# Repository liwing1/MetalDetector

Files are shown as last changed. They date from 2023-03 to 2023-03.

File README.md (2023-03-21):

# Processo Seletivo HealthGo - Projeto Detector de Metais

# Objetivo

Projetar um detector de metais para garantir a segurança dos pacientes antes de exames.

Condições:

    - Chave liga/desliga;
    - LED de indicação de alimentação do sistema;
    - Botão para habilitar/desabilitar detecção;
    - LED de indicção de detecção habilitada;
    - Buzzer de sinalização na presença de metal.

# Hardware

O primeiro passo para a realização do projeto é montar um diagrama em alto nível de abstração:

diagrama

Com essas informações já é possível construir uma lista de componentes que será necessário para o funcionamento de cada bloco.

## 1. Regulação de Tensão

Tendo em vista que todos os componentes dependem de redução da tensão para funcionarem, foi primeiramente projetado o regulador de tensão.

power

Optou-se pela utilização do LM296 devido a sua grande disponibilidade no mercado e alta performance. Vale ainda salientar que o LED de indicação de alimentação foi posicionado após a regulação da tensão. Assim, fica evidente que os demais componentes estão sendo alimentado corretamente.

## 2. Microcontrolador

A tarefa de ler os registros de um sensor através de comunicação serial é muito simples. No entanto, por se tratar da segurança de pacientes, deve-se ser cauteloso com a escolha do processador.

uc

O ESP32-WROOM-32 foi escolhido por sua robustez tanto no hardware quanto no software.

## 3. Sensor 

O sensor indutivo foi previamente definido, incluindo a impendância indutiva que é acoplada ao chip. Para que seja atingida a frequência de ressonância de 3MHz no tanque LC, a capacitância adicionada em paralelo deve ser calculada através da equação 1 fornecida no datasheet do fabricante:

fsensor

O valor obtido foi de 390.89 pF. Entretando, o valor comercial mais próximo é de 390 pF, que está dentro da faixa de erro do próprio capacitor.

sensor

Nota-se ainda que além da comunicação serial com o microcontrolador, é necessário também o fornecimento de um sinal de clock externo que serve como referência interna para a amostragem do sinal (a recomendação do fabricante é 16MHz).

# Firmware

Da mesma forma que o hardware é separado de forma modular através de blocos funcionais, é interessante que o software mantenha a mesma estrutura. Assim, o código pode ser reaproveitado com mais facilidade.

Ademais, apesar de o Arduino ser uma das plataformas de desenvolvimento mais populares, optou-se pela utilização do framework oficial da Espressif, o ESP-IDF. Neste ambiente a inclusão de bibliotecas é mais simples graças ao CMake. Além disso a API permite um controle mais preciso sobre os periféricos.

## 1. Porte da Lib

Para importar a biblioteca fornecida ao ESP-IDF foi necessário transforma-la em um _component_ através do arquivo CMakeLists.txt:
```C
idf_component_register(SRCS "ldc1101_driver.c" "ldc1101_hal.c"
                    INCLUDE_DIRS "."
                    PRIV_REQUIRES driver)
```

Após esse passo o biblioteca ja passa a ser compilável. No entanto, por ser um código genérico para qualquer arquitetura, é necessário adicionar a camada de abstração de hardware (HAL) específica do ESP.

```C
void hal_spiMap(T_HAL_P spiObj)
{
    T_HAL_SPI_OBJ tmp = (T_HAL_SPI_OBJ)spiObj;

    spi_bus_config_t spi_bus_config = {
        .mosi_io_num = tmp->mosi_io_num,
        .miso_io_num = tmp->miso_io_num,
        .sclk_io_num = tmp->sclk_io_num,
        .quadwp_io_num = PIN_NOT_USED,
        .quadhd_io_num = PIN_NOT_USED,
        .max_transfer_sz = 32,
    };

    spi_device_interface_config_t spi_device_interface_config = {
        .mode = 2,                  //POL:1; PHA:0
        .clock_speed_hz = tmp->clk_speed_hz,
        .queue_size = 1,
        .spics_io_num = PIN_NOT_USED,
        .pre_cb = NULL,
        .post_cb = NULL,
    };

    spi_bus_initialize(SPI2_HOST, &spi_bus_config, SPI_DMA_CH_AUTO);
    spi_bus_add_device(SPI2_HOST, &spi_device_interface_config, &spi_handle);
}

void hal_spiWrite(uint8_t *pBuf, uint16_t nBytes)
{
    spi_transaction_t transaction = {
        .tx_buffer = pBuf,
        .length = nBytes
    };
    spi_device_polling_transmit(spi_handle, &transaction);
}

void hal_spiRead(uint8_t *pBuf, uint16_t nBytes)
{
    spi_transaction_t transaction = {
        .rx_buffer = pBuf,
        .length = nBytes
    };
    spi_device_polling_transmit(spi_handle, &transaction);
}
```

## 2. Inicialização
Depois de inicializar os periféricos de interação com o usuário e o clock externo, o ESP pode finalmente se comunicar com o sensor. Utilizando-se da biblioteca fornecida pela MIKROE, a configuração e leitura do sensor fica muito simplificada.

```C
void applicationInit()
{
    _LDC1101_SPI_INTERFACE spi_interface ={
        .miso_io_num = 12,
        .mosi_io_num = 13,
        .sclk_io_num = 14,
        .clk_speed_hz = 8000000,
    };
    ldc1101_spiDriverInit( (T_LDC1101_P)&spi_interface );
    ldc1101_init();

    // Valores otimizados da ref: http://www.ti.com/lit/zip/slyc137
    // RPmax = 12k; RPmin = 3k
    ldc1101_writeByte(_LDC1101_REG_CFG_RP_MEASUREMENT_DYNAMIC_RANGE,_LDC1101_RP_SET_RP_MAX_12KOhm | _LDC1101_RP_SET_RP_MIN_3KOhm);
    // C1 = 6pF; R1 = 41.63k
    ldc1101_writeByte(_LDC1101_REG_CFG_INTERNAL_TIME_CONSTANT_1,_LDC1101_TC1_C1_6pF | 0x1D);
    // C2 = 24pF; R2 = 97.5k
    ldc1101_writeByte(_LDC1101_REG_CFG_INTERNAL_TIME_CONSTANT_2,_LDC1101_TC2_C2_24pF | 0x39);
    // MINfreq = 7MHz; RESPtime = 192s
    ldc1101_writeByte(_LDC1101_REG_CFG_RP_L_CONVERSION_INTERVAL, 0xD0 | _LDC1101_DIG_CFG_RESP_TIME_192s);

    ldc1101_setPowerMode(_LDC1101_FUNC_MODE_ACTIVE_CONVERSION_MODE);
    
    ldc1101_goTo_RPmode();
    ESP_LOGW(LDC1101_TAG, "--- Start measurement ---");
}
```

## 3. Laço Principal

Graças ao FreeRTOS foi possível subdividir o programa em duas tarefas que são processadas de forma independente.

```C
void button_task(void* arg)
{
    uint32_t io_num;
    while(1)
    {
        // Entra neste if quando botão é precionado
        if(xQueueReceive(gpio_evt_queue, &io_num, portMAX_DELAY)) {
            
            sensor_state = !sensor_state; //toggle sensor

            led_set_level(sensor_state == SENSOR_OCIOSO ? LED_OFF:LED_ON);
        }
        vTaskDelay(100/portTICK_PERIOD_MS);
    }
}
```

Essa primeira tarefa monitora o status da fila, que só é preenchida quando o botão é pressionado, o que aciona a interrupção:

```C
static void IRAM_ATTR gpio_isr_handler(void* arg)
{
    uint32_t gpio_num = (uint32_t) arg;
    xQueueSendFromISR(gpio_evt_queue, &gpio_num, NULL);
}
```

Assim, a indicação do LED é habilitada/desabilitada e o estado do sensor também é trocado.

```C
void ldc1101_task()
{   
    while(1)
    {
        uint16_t RP_Data = 0;
        float Rp = 0;

        switch(sensor_state)
        {
            case SENSOR_OCIOSO:
                buzzer_set_level(BUZZER_OFF);

            break;

            case SENSOR_DETECT:
                RP_Data = ldc1101_getRPData();
                // Calcular Rp pela eq 4
                Rp = (12000 * 3000)/((12000 * (1-RP_Data/65535)) + (3000 * (RP_Data/65535)));

                buzzer_set_level(Rp < RP_TRESHOLD ? BUZZER_ON:BUZZER_OFF);
                ESP_LOGW(LDC1101_TAG, "Inductive Linear Position: %d", RP_Data);
                
            break;
        }

        vTaskDelay(100/portTICK_PERIOD_MS);
    }
}
```

É nesta task que ocorre a leitura do sensor de fato. Para determinar se o metal foi detectado estimou-se o valor máximo de Rp quando p sensor está interagindo com algum material condutor. Apartir disso definiu-se que o treshold é o valor intermediário entre o Rp máximo e o Rp mínimo. 

Mas é importante ressaltar que apesar de esses parâmetros serem fornecidos pelo fábricante, não se deve deixar de realizar ajustes práticos. Pois capacitancias parasitas e variação da temperatura podem afetar drasticamente as medições.

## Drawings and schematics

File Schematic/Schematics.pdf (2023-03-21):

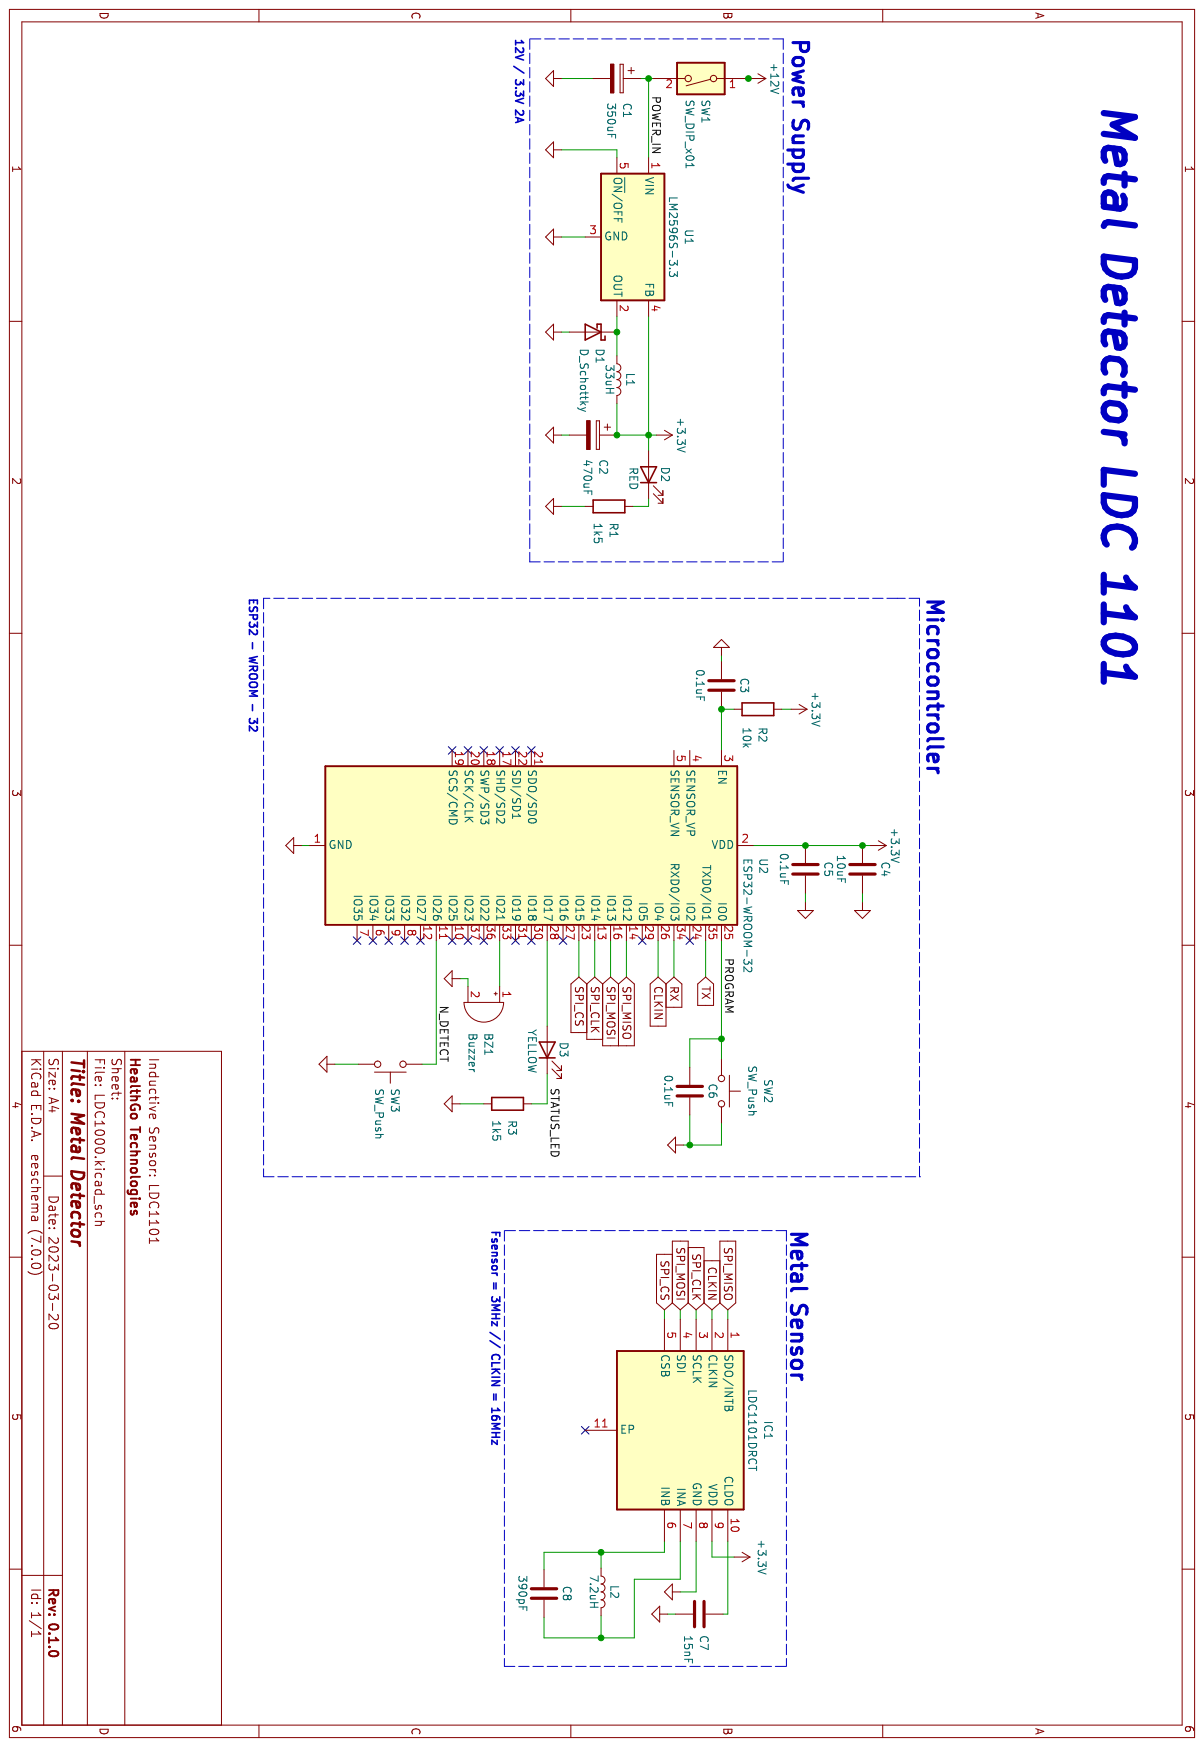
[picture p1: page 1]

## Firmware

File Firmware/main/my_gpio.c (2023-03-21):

#include "my_gpio.h"
#include "driver/gpio.h"
#include "driver/ledc.h"

#define PIN_STATUS_LED  GPIO_NUM_17
#define PIN_BUZZER      GPIO_NUM_21
#define PIN_BUTTON      GPIO_NUM_26

#define PIN_CLKIN       GPIO_NUM_4

QueueHandle_t gpio_evt_queue = NULL;

static void IRAM_ATTR gpio_isr_handler(void* arg)
{
    uint32_t gpio_num = (uint32_t) arg;
    xQueueSendFromISR(gpio_evt_queue, &gpio_num, NULL);
}

void init_gpio(void)
{
    // Config BUTTON
    gpio_config_t io_conf = {
        .intr_type = GPIO_INTR_NEGEDGE,
        .mode = GPIO_MODE_INPUT,
        .pin_bit_mask = (1ULL<<PIN_BUTTON),
        .pull_down_en = GPIO_PULLDOWN_DISABLE,
        .pull_up_en = GPIO_PULLUP_ENABLE,
    };
    gpio_config(&io_conf);
    gpio_set_intr_type(PIN_BUTTON, GPIO_INTR_ANYEDGE);

    gpio_install_isr_service(0);
    gpio_isr_handler_add(PIN_BUTTON, gpio_isr_handler, (void*) PIN_BUTTON);
    gpio_evt_queue = xQueueCreate(10, sizeof(uint32_t));


    // Config BUZZER
    io_conf.mode = GPIO_MODE_OUTPUT;
    io_conf.pull_up_en = GPIO_PULLUP_DISABLE;
    io_conf.pin_bit_mask = (1ULL<<PIN_BUZZER);
    gpio_config(&io_conf);

    // CONFIG LED
    io_conf.pin_bit_mask = (1ULL<<PIN_STATUS_LED);
    gpio_config(&io_conf);
}

void init_pwm(void)
{
    // Prepare and then apply the LEDC PWM timer configuration
    ledc_timer_config_t ledc_timer = {
        .speed_mode       = LEDC_HIGH_SPEED_MODE,
        .timer_num        = LEDC_TIMER_0,
        .duty_resolution  = LEDC_TIMER_1_BIT,
        .freq_hz          = 16000000,  // Set output frequency at 16 MHz
        .clk_cfg          = LEDC_AUTO_CLK
    };
    ESP_ERROR_CHECK(ledc_timer_config(&ledc_timer));

    // Prepare and then apply the LEDC PWM channel configuration
    ledc_channel_config_t ledc_channel = {
        .speed_mode     = LEDC_HIGH_SPEED_MODE,
        .channel        = LEDC_CHANNEL_0,
        .timer_sel      = LEDC_TIMER_0,
        .intr_type      = LEDC_INTR_DISABLE,
        .gpio_num       = PIN_CLKIN,
        .duty           = 0, // Set duty to 50%
        .hpoint         = 0
    };
    ESP_ERROR_CHECK(ledc_channel_config(&ledc_channel));

    // Set duty to 50%
    ESP_ERROR_CHECK(ledc_set_duty(LEDC_HIGH_SPEED_MODE, LEDC_CHANNEL_0, 1));
    // Update duty to apply the new value
    ESP_ERROR_CHECK(ledc_update_duty(LEDC_HIGH_SPEED_MODE, LEDC_CHANNEL_0));
}

void led_set_level(led_level_t led_level)
{
    gpio_set_level(PIN_STATUS_LED, led_level);
}

void buzzer_set_level(buzzer_level_t buzzer_level)
{
    gpio_set_level(PIN_BUZZER, buzzer_level);
}

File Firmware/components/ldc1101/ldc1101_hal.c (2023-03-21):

/*
    __ldc1101_hal.c
    
-----------------------------------------------------------------------------

  This file is part of mikroSDK.

  Copyright (c) 2017, MikroElektonika - http://www.mikroe.com

  All rights reserved.

----------------------------------------------------------------------------- */

/**  
@file  __ldc1101_hal.c
@brief   LDC1101 HAL Interface
*/
/**
@defgroup   LDC1101_HAL
@brief      LDC1101 HAL Interface
@{

| Global Library Prefix | **HAL**            |
|:---------------------:|:------------------:|
| Version               | **3.2.0**          |
| Date                  | **Sep 2017**       |
| Developer             | **MikroE FW Team** |

*/
/* -------------------------------------------------------------------------- */

#include "stdint.h"
#include "driver/spi_master.h"

/** 
 * HAL Global Abstract Type
 */
#define T_HAL_P         const uint32_t*      

#define T_HAL_SPI_OBJ   const T_hal_spiObj*
#define T_HAL_I2C_OBJ   const T_hal_i2cObj*
#define T_HAL_UART_OBJ  const T_hal_uartObj*
#define T_HAL_GPIO_OBJ  const T_hal_gpioObj*

/** @defgroup LDC1101_HAL_COMPILE HAL Cofiguration */            /** @{ */

                 #define   __HAL_SPI__                            /**<     @macro __HAL_SPI__  @brief SPI HAL selector */                
//                #define   __HAL_I2C__                            /**<     @macro __HAL_I2C__  @brief I2C HAL selector */
//               #define   __HAL_UART__                           /**<     @macro __HAL_UART__  @brief UART HAL selector */                          

// #define   __AN_PIN_INPUT__          0
// #define   __RST_PIN_INPUT__         1
// #define   __CS_PIN_INPUT__          2
// #define   __SCK_PIN_INPUT__         3
#define   __MISO_PIN_INPUT__        12                                   
// #define   __MOSI_PIN_INPUT__        5
  #define   __PWM_PIN_INPUT__         6                                  
  #define   __INT_PIN_INPUT__         7
// #define   __RX_PIN_INPUT__          8                              
// #define   __TX_PIN_INPUT__          9
// #define   __SCL_PIN_INPUT__         10                                  
// #define   __SDA_PIN_INPUT__         11  

// #define   __AN_PIN_OUTPUT__         0
// #define   __RST_PIN_OUTPUT__        1                                   
#define   __CS_PIN_OUTPUT__         15                              
#define   __SCK_PIN_OUTPUT__        14
// #define   __MISO_PIN_OUTPUT__       4                                    
#define   __MOSI_PIN_OUTPUT__       13
// #define   __PWM_PIN_OUTPUT__        6                                    
// #define   __INT_PIN_OUTPUT__        7
// #define   __RX_PIN_OUTPUT__         8                                
// #define   __TX_PIN_OUTPUT__         9
// #define   __SCL_PIN_OUTPUT__        10                                    
// #define   __SDA_PIN_OUTPUT__        11    
#define PIN_NOT_USED    -1
                                                                       /** @} */
#ifdef __HAL_SPI__

static spi_device_handle_t spi_handle;

/** @defgroup LDC1101_HAL_SPI HAL SPI Interface */               /** @{ */


typedef struct
{
    int mosi_io_num;
    int miso_io_num;
    int sclk_io_num;
    int clk_speed_hz;
} T_hal_spiObj;

/**
 * @brief Map SPI Function Pointers
 */
void hal_spiMap(T_HAL_P spiObj)
{
    T_HAL_SPI_OBJ tmp = (T_HAL_SPI_OBJ)spiObj;

    spi_bus_config_t spi_bus_config = {
        .mosi_io_num = tmp->mosi_io_num,
        .miso_io_num = tmp->miso_io_num,
        .sclk_io_num = tmp->sclk_io_num,
        .quadwp_io_num = PIN_NOT_USED,
        .quadhd_io_num = PIN_NOT_USED,
        .max_transfer_sz = 32,
    };

    spi_device_interface_config_t spi_device_interface_config = {
        .mode = 2,                  //POL:1; PHA:0
        .clock_speed_hz = tmp->clk_speed_hz,
        .queue_size = 1,
        .spics_io_num = PIN_NOT_USED,
        .pre_cb = NULL,
        .post_cb = NULL,
    };

    spi_bus_initialize(SPI2_HOST, &spi_bus_config, SPI_DMA_CH_AUTO);
    spi_bus_add_device(SPI2_HOST, &spi_device_interface_config, &spi_handle);
}

/**
 * @brief hal_spiWrite
 *
 * @param[in] pBuf             pointer to data buffer
 * @param[in] nBytes           number of bytes for writing
 *
 * Function executes write sequence of n bytes.
 *
 * @note
 * This function have not using CS pin.
 */
void hal_spiWrite(uint8_t *pBuf, uint16_t nBytes)
{
    spi_transaction_t transaction = {
        .tx_buffer = pBuf,
        .length = nBytes
    };
    spi_device_polling_transmit(spi_handle, &transaction);
}

/**
 * @brief hal_spiRead
 *
 * @param[out] pBuf            pointer to data buffer
 * @param[in]  nBytes          number of bytes for writing
 *
 * Function executes read sequence of n bytes.
 *
 * @note
 * This function should not use CS pin.
 */
void hal_spiRead(uint8_t *pBuf, uint16_t nBytes)
{
    spi_transaction_t transaction = {
        .rx_buffer = pBuf,
        .length = nBytes
    };
    spi_device_polling_transmit(spi_handle, &transaction);
}

/**
 * @brief hal_spiTransfer
 *
 * @param[in]  pIn             pointer to write data buffer
 * @param[out] pOut            pointer to read data buffer
 * @param[in]  nBytes          number of bytes for writing
 *
 * Function should executes read/write sequence of n bytes.
 *
 * @note
 * This function should not use CS pin.
 */
void hal_spiTransfer(uint8_t *pIn, uint8_t *pOut, uint16_t nBytes);

                                                                       /** @} */
#endif
#ifdef __HAL_I2C__

/** @defgroup LDC1101_HAL_I2C HAL I2C Interface */               /** @{ */

/**
 * @brief Map I2C Function Pointers
 */
void hal_i2cMap(T_HAL_P i2cObj);

/**
 * @brief hal_i2cStart
 *
 * @return    0                No Error
 *
 * Function executes start condition on I2C BUS.
 */
static int hal_i2cStart(void);

/**
 * @brief hal_i2cWrite
 *
 * @param[in] slaveAddress     7 bit slave addres without 0 bit (read/write bit)
 * @param[in] pBuf             pointer to data buffer
 * @param[in] nBytes           number of bytes for writing
 * @param[in] endMode          END_MODE_STOP / END_MODE_RESTART / END_MODE_NO
 *
 * @return    0                No Error
 *
 * Function should executes write sequence on I2C bus.
 *
 * |       8 Bits      | Write Sequence (n Bytes) | End Mode       |
 * |:-----------------:|:------------------------:|:--------------:|
 * | Slave Address + W | Data Bytes               | Stop / Restart |
 *
 * @note
 * This function alongside with hal_i2cStart represents comlete write sequence.
 *
 * @warning
 * No End mode is not possible on all architectures.
 */
static int hal_i2cWrite(uint8_t slaveAddress, uint8_t *pBuf, uint16_t nBytes, uint8_t endMode);

/**
 * @brief hal_i2cRead
 *
 * @param[in] slaveAddress     7 bit slave addres without 0 bit (read/write bit)
 * @param[in] pBuf             pointer to data buffer
 * @param[in] nBytes           number of bytes to read
 * @param[in] endMode          END_MODE_STOP / END_MODE_RESTART / END_MODE_NO
 *
 * @return    0                No Error
 *
 * Function should executes read sequence on I2C bus.
 * 
 * |       8 Bits      | Read Sequence (n Bytes)  | End Mode       |
 * |:-----------------:|:------------------------:|:--------------:|
 * | Slave Address + R | Data Bytes + ACK/NACK    | Stop / Restart |
 *
 * @note
 * This function alongside with hal_i2cStart represents comlete read sequence.
 *
 * @warning
 * No End mode is not possible on all architectures.
 */
static int hal_i2cRead(uint8_t slaveAddress, uint8_t *pBuf, uint16_t nBytes, uint8_t endMode);

                                                                       /** @} */
#endif
#ifdef __HAL_UART__

/** @defgroup LDC1101_HAL_UART HAL UART Interface */             /** @{ */

/**
 * @brief Map UART Function Pointers
 */
void hal_uartMap(T_HAL_P uartObj);

/**
 * @brief hal_uartWrite
 *
 * @param[in] input tx data byte
 *
 * Function writes one byte on UART.
 */
void hal_uartWrite(uint8_t input);

/**
 * @brief hal_uartRead
 *
 * @return rx data byte
 *
 * Function reads one byte.
 */
static uint8_t hal_uartRead();

/**
 * @brief hal_uartReady
 *
 * @return rx buffer state
 *
 * Function should return 1 if rx buffer have received new data.
 */
static uint8_t hal_uartReady();
                                                                       /** @} */
#endif

/** @defgroup LDC1101_HAL_GPIO HAL GPIO Interface */             /** @{ */

typedef void    (*T_hal_gpioSetFp)(uint8_t);                         
typedef uint8_t (*T_hal_gpioGetFp)();

typedef struct
{
    T_hal_gpioSetFp      gpioSet[ 12 ];
    T_hal_gpioGetFp      gpioGet[ 12 ];
  
}T_hal_gpioObj;

#ifdef __AN_PIN_INPUT__
static T_hal_gpioGetFp          hal_gpio_anGet; 
#endif
#ifdef __CS_PIN_INPUT__
static T_hal_gpioGetFp          hal_gpio_csGet; 
#endif
#ifdef __RST_PIN_INPUT__
static T_hal_gpioGetFp          hal_gpio_rstGet; 
#endif
#ifdef __SCK_PIN_INPUT__
static T_hal_gpioGetFp          hal_gpio_sckGet; 
#endif
#ifdef __MISO_PIN_INPUT__
static T_hal_gpioGetFp          hal_gpio_misoGet; 
#endif
#ifdef __MOSI_PIN_INPUT__
static T_hal_gpioGetFp          hal_gpio_mosiGet; 
#endif
#ifdef __PWM_PIN_INPUT__
static T_hal_gpioGetFp          hal_gpio_pwmGet; 
#endif
#ifdef __INT_PIN_INPUT__
static T_hal_gpioGetFp          hal_gpio_intGet; 
#endif
#ifdef __RX_PIN_INPUT__   
static T_hal_gpioGetFp          hal_gpio_rxGet; 
#endif
#ifdef __TX_PIN_INPUT__   
static T_hal_gpioGetFp          hal_gpio_txGet; 
#endif
#ifdef __SCL_PIN_INPUT__  
static T_hal_gpioGetFp          hal_gpio_sclGet; 
#endif
#ifdef __SDA_PIN_INPUT__  
static T_hal_gpioGetFp          hal_gpio_sdaGet; 
#endif
#ifdef __AN_PIN_OUTPUT__  
static T_hal_gpioSetFp          hal_gpio_anSet;  
#endif
#ifdef __CS_PIN_OUTPUT__
static T_hal_gpioSetFp          hal_gpio_csSet;  
#endif
#ifdef __RST_PIN_OUTPUT__ 
static T_hal_gpioSetFp          hal_gpio_rstSet;  
#endif
#ifdef __SCK_PIN_OUTPUT__ 
static T_hal_gpioSetFp          hal_gpio_sckSet;  
#endif
#ifdef __MISO_PIN_OUTPUT__
static T_hal_gpioSetFp          hal_gpio_misoSet;  
#endif
#ifdef __MOSI_PIN_OUTPUT__
static T_hal_gpioSetFp          hal_gpio_mosiSet;  
#endif
#ifdef __PWM_PIN_OUTPUT__ 
static T_hal_gpioSetFp          hal_gpio_pwmSet;  
#endif
#ifdef __INT_PIN_OUTPUT__ 
static T_hal_gpioSetFp          hal_gpio_intSet;  
#endif
#ifdef __RX_PIN_OUTPUT__  
static T_hal_gpioSetFp          hal_gpio_rxSet;  
#endif
#ifdef __TX_PIN_OUTPUT__  
static T_hal_gpioSetFp          hal_gpio_txSet;  
#endif
#ifdef __SCL_PIN_OUTPUT__ 
static T_hal_gpioSetFp          hal_gpio_sclSet;  
#endif
#ifdef __SDA_PIN_OUTPUT__ 
static T_hal_gpioSetFp          hal_gpio_sdaSet;  
#endif                              

/**
 * @brief Map GPIO Function pointers
 */
void hal_gpioMap(T_HAL_P gpioObj)
{
    T_HAL_GPIO_OBJ tmp = (T_HAL_GPIO_OBJ)gpioObj;
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

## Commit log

2023-03-20 add schematic
    [LDC1000.kicad_pcb, LDC1000.kicad_sch]
2023-03-20 add button to start detection
    [LDC1000.kicad_sch]
2023-03-21 update firmware
    [LDC1000.kicad_sch]
2023-03-21 fix current voltage regulator
    [LDC1000.kicad_sch]
